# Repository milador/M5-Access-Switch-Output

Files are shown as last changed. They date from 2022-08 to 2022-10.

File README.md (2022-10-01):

# M5-Access-Switch-Output

A Wi-Fi enabled Adaptive Switch Output device based on ESP32 M5StickC/M5StickCPlus which offers up to two 3.5mm switch outputs. The M5 Switch Output can be used to operate up to two switch adapted devices.

<p align="center">
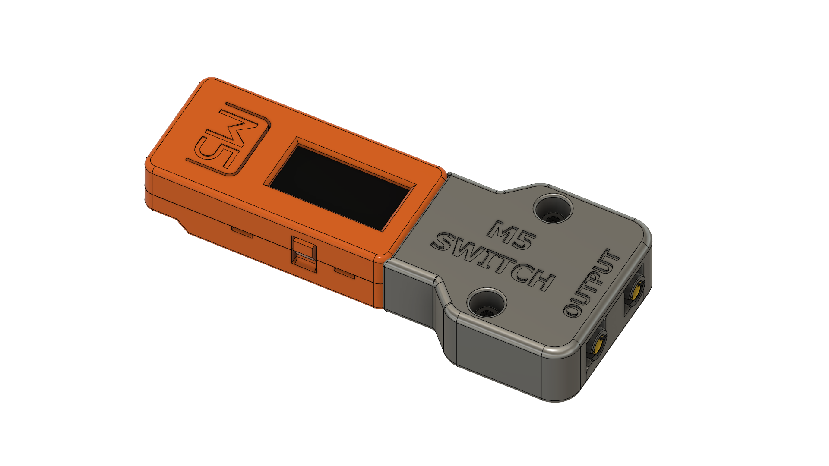
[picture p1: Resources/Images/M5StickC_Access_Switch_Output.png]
M5StickC_Access_Switch_Output

</p>

## Requirements and setup instructions 
The setup process is divided to three main catagories:

  1. [Hardware](./Hardware/) : The required hardware and design files
  2. [Software](./Software/) : The required software
  3. [Documentation](./Documentation/) : The assembly guide,user guide and other documents 

## License

### MIT License

Copyright (c) 2022 milador

Permission is hereby granted, free of charge, to any person obtaining a copy of this software and associated documentation files (the "Software"), to deal in the Software without restriction, including without limitation the rights to use, copy, modify, merge, publish, distribute, sublicense, and/or sell copies of the Software, and to permit persons to whom the Software is furnished to do so, subject to the following conditions:

The above copyright notice and this permission notice shall be included in all copies or substantial portions of the Software.

THE SOFTWARE IS PROVIDED "AS IS", WITHOUT WARRANTY OF ANY KIND, EXPRESS OR IMPLIED, INCLUDING BUT NOT LIMITED TO THE WARRANTIES OF MERCHANTABILITY, FITNESS FOR A PARTICULAR PURPOSE AND NONINFRINGEMENT. IN NO EVENT SHALL THE AUTHORS OR COPYRIGHT HOLDERS BE LIABLE FOR ANY CLAIM, DAMAGES OR OTHER LIABILITY, WHETHER IN AN ACTION OF CONTRACT, TORT OR OTHERWISE, ARISING FROM, OUT OF OR IN CONNECTION WITH THE SOFTWARE OR THE USE OR OTHER DEALINGS IN THE SOFTWARE.

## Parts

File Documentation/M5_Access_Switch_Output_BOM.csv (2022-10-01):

Index | Quantity | Component | Digikey Part Number | Manufacturer Part Number | Description | Unit Price (CAD) | Price (CAD) | Link
1 | 1 |  | 2221-K016-P-ND | K016-P | M5STICKC PLUS ESP32-PICO IOT KIT | 31.48 | 31.48 | https://www.digikey.ca/en/products/detail/m5stack-technology-co-ltd/K016-P/13148797
2 | 2 | SW1,SW2 | CP-43514-ND | SJ-43514 | CONN JACK 4COND 3.5MM | 1.48 | 2.96 | https://www.digikey.ca/en/products/detail/SJ-43514/CP-43514-ND/368146
3 | 2 | K1,K2 | Z5417-ND | G3VM-41AY1 | SSR RELAY SPST-NO 2A 0-40V | 5.54 | 11.08 | https://www.digikey.ca/en/products/detail/omron-electronics-inc-emc-div/G3VM-41AY1/5799756
4 | 1 | JP1 | 609-3321-ND | 68016-208HLF | CONN HEADER R/A 8POS 2.54MM | 0.7 | 0.7 | https://www.digikey.ca/en/products/detail/amphenol-cs-fci/68016-208HLF/1878499
5 | 2 | R1,R2 | S220QCT-ND | CFM14JT220R | RES 220 OHM 5% 1/4W AXIAL | 0.15 | 0.3 | https://www.digikey.ca/en/products/detail/stackpole-electronics-inc/CFM14JT220R/1742139
6 | 2 | N/A | 145-50M025045P006-ND | 50M025045P006 | PAN PHILLIPS SCREW, M2.5 X 4.5 T | 0.23 | 0.46 | https://www.digikey.ca/en/products/detail/essentra-components/50M025045P006/11638590
7 | 2 | N/A | 36-9600-ND | 9600 | HEX NUT 1/4" STEEL 4-40 | 0.16 | 0.32 | https://www.digikey.ca/en/products/detail/keystone-electronics/9600/2746248
 |  |  |  |  |  | Total Price (CAD) | 46.52

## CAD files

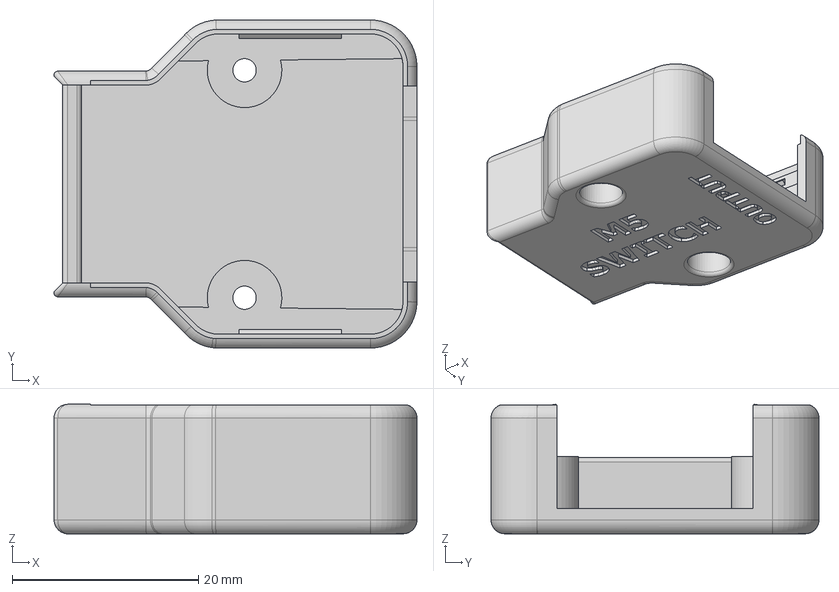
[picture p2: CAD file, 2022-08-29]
Hardware/Case/STEP/M5StickC_Switch_Output_Main.step
38.9 x 35.2 x 13.9 mm

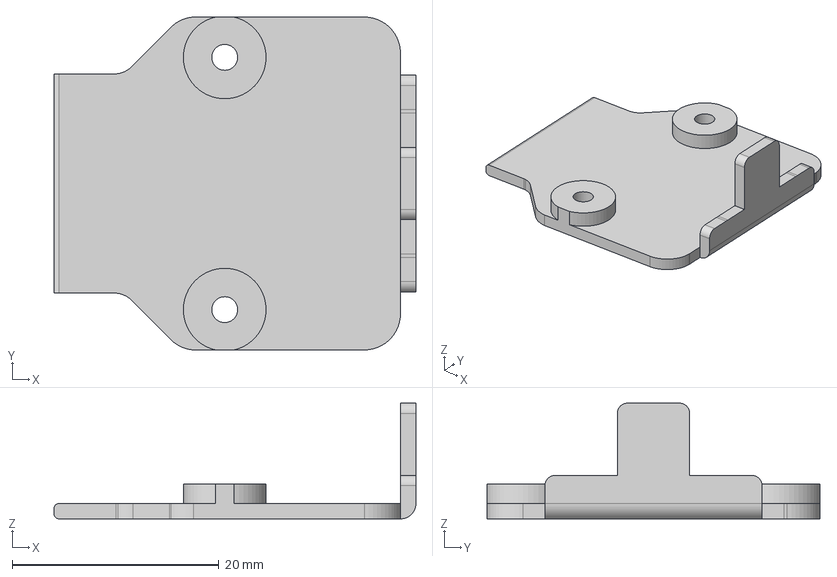
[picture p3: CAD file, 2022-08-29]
Hardware/Case/STEP/M5StickC_Switch_Output_Bottom.step
35.0 x 32.2 x 11.2 mm

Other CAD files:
Hardware/Case/STL/M5StickC_Switch_Output_Bottom.stl
Hardware/Case/STL/M5StickC_Switch_Output_Main.stl

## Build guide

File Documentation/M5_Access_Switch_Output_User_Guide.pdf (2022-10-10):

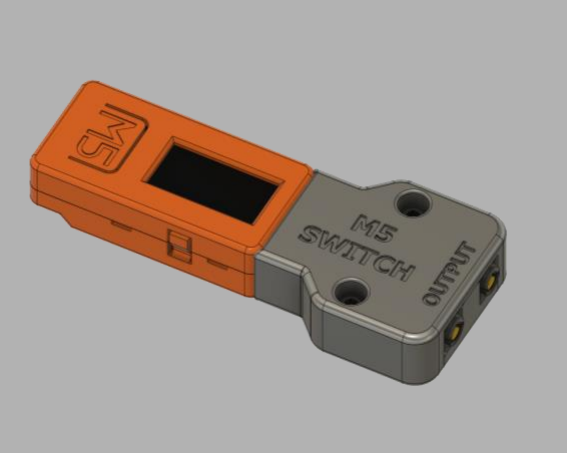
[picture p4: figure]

# M5 ACCESS SWITCH OUTPUT USER GUIDE (V1.0)

A wireless switch output device

### Milad Hajihassan

https://github.com/milador/M5-Access-Switch-Output

1

## Contents

Usage requirements | 2
Usage Components | 2
Usage Process | 2
How to Use? | 2
Sleep Mode | 2

2

## Usage requirements

### Usage Components

1. Mono Audio Jack Cable x 2

## Usage Process

### How to Use?

1. Connect the Switch Output module through two 3.5mm Mono Audio jack cables to two

adapted devices.

1.1. Switch A
1.2. Switch B
2. Connect to the Access Point (Example: Windows 10 PC)

On Windows 10:

2.1. Select Start > Settings > Network & Internet > Show available networks. Select

M5SwitchOutput network and click on connect. The default network password is

12345678.

3. M5StackC will display an IP address on its display screen.
4. Open your favourite web browser software.
5. Enter the IP address from step 3 to access switch output control web page.
6. You can now send switch actions by pressing each switch button.

Sleep Mode

The device goes to sleep mode if it’s not used for more than one minute and automatically wakes up every 3 minutes.

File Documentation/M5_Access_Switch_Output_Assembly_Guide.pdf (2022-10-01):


# M5 ACCESS SWITCH OUTPUT ASSEMBLY GUIDE (V1.0)

A wireless switch output device

### Milad Hajihassan

https://github.com/milador/M5-Access-Switch-Output

1

## Contents

Components List | 2
Software | 3
Installing Arduino IDE | 3
Installing Arduino Libraries | 3
Board Support Packages | 3
Required Software and libraries | 3
Uploading Software | 4
Hardware Assembly | 5
Enclosure design | 5
M5 Access Switch Output Assembly | 6

2

## Components List

1. M5STICKC PLUS ESP32-PICO IOT KIT x 1
2. SJ-43514 3.5MM TRRS AUDIO JACK x 2
3. G3VM-41AY1 SSR RELAY x 2
4. 8 POSITION MALE RIGHT ANGLE HEADER x 1
5. 220 OHM 1/4W RESISTOR x 2
6. M2.5 SCREW (8MM) x 2
7. M2.5 SCREW NUT x 2

The bill of materials can also be downloaded from GitHub repository under main directory. (https://github.com/milador/M5-Access-Switch-Output/blob/main/Documentation/M5_Access_Switch_Output_BOM.csv)

https://github.com/milador/M5-Access-Switch-

Output/blob/main/Documentation/M5_Access_Switch_Output_BOM.csv

3

## Software

The Switch Output software can be downloaded from the GitHub repository under software directory.

https://raw.githubusercontent.com/milador/M5-Access-Switch-Output/main/Software/M5_Access_Switch_Output_Software/M5_Access_Switch_Output_Software.ino (https://raw.githubusercontent.com/milador/M5-Access-Switch-Output/main/Software/M5_Access_Switch_Output_Software/M5_Access_Switch_Output_Software.ino)

### Installing Arduino IDE

The Arduino IDE is required to compile and upload the source code to the MCU in your M5StickC device. You can download and install the Arduino from official Arduino website that you can find using following link:

https://www.arduino.cc/en/software

### Installing Arduino Libraries

The following instructions on how to install additional Arduino libraries helps you to get started with setting up Arduino IDE with required libraries and dependencies.

https://www.arduino.cc/en/guide/libraries

Board Support Packages
You can find the official instructions to install Board Support Packages on M5Stack website using following link:

https://docs.m5stack.com/en/quick_start/m5stickc/arduino

Alternatively, you can perform following instructions to install Board Support Packages:

1. Open and start the Arduino IDE.
2. Go to File > Preferences.
3. Add following link as a new line under Additional Board Manager URLs
- https://m5stack.oss-cnshenzhen.aliyuncs.com/resource/arduino/package_m5stack_index.json (https://m5stack.oss-cn-shenzhen.aliyuncs.com/resource/arduino/package_m5stack_index.json)
4. Restart the Arduino IDE
5. Open the Boards Manager option from the Tools > Board menu and install M5Stack by M5Stack official
6. Wait until the IDE finishes installing the cross-compiling toolchain and tools associated with Board Support Package. This may take few minutes.
7. That’s it! The installation of Board Support Packages is finished.

Required Software and libraries
The software requirements:
- M5_Access_Switch_Output_Software.ino (https://raw.githubusercontent.com/milador/M5-Access-Switch-Output/develop/Software/M5_Access_Switch_Output_Software/M5_Access_Switch_Output_Software.ino)
- M5StickC Plus (https://github.com/m5stack/M5StickC-Plus)

You can use the following instructions to download and install the required libraries:

1) Visit the M5StickC-Plus library github repository page.
2) Click on Code > Download Zip to download M5StickC-Plus.

4

3) Extract M5StickC-Plus-master.zip file
4) Rename M5StickC-Plus-master folder to M5StickC-Plus folder under M5StickC-Plus-master subdirectory.
5) Copy or move M5StickC-Plus folder to Arduino installation library subdirectory. As an example: This is found under C:\Program Files (x86)\Arduino\libraries in windows 10.
6) Visit the M5_Access_Switch_Output_Software.ino raw source code file under Software directory.
7) Right click on the source code or any place on this page and select Save Page As…
8) Select the directory you would like to save the software in your computer.
9) Change File name from M5_Access_Switch_Output_Software to M5_Access_Switch_Output_Software.ino
10) Change Save as type to All Files.
11) Click on Save button.
12) Open the directory you selected in step 8.
13) Double left click or open M5_Access_Switch_Output_Software file
14) Arduino IDE will ask your permission to create a new sketch folder named M5_Access_Switch_Output_Software and move M5_Access_Switch_Output_Software.ino under this folder.
15) Click on the Ok button.
16) Arduino IDE should now open the M5_Access_Switch_Output_Software.ino file automatically.

Uploading Software
Note: Make sure all files are included in your local copy of Software directory before uploading it to the M5StickC device. The libraries can be installed in Arduino libraries.

You can go ahead and upload the downloaded M5_Access_Switch_Output_Software.ino code to M5StickC using Arduino IDE once all the necessary libraries are installed.

1. Start the Arduino IDE
2. Open M5_Access_Switch_Output_Software.ino
3. Select the Board under Tools > Board > M5Stick Arduino Boards as M5Stick-C-Plus
4. Select the correct port number under Tools > Port which should show COM XX (M5Stick-C-Plus)

Note: It’s very important to make sure the correct Board and port number are selected as selecting the wrong board may result problems with bootloader of M5StickC device.

5. Press the Verify button to make sure there is no problem with the software and libraries.
6. Press Upload button

You can now go ahead and upload the software. Arduino IDE will show you a Done Uploading message indicating the software is uploaded to your M5StickC device.

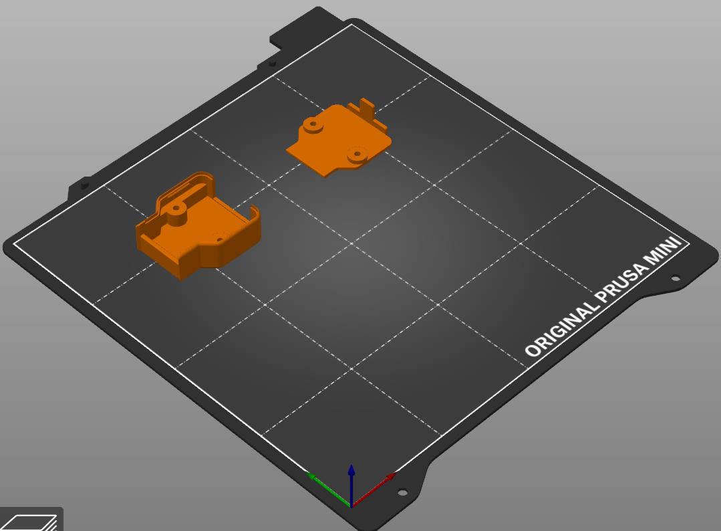
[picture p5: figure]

5

## Hardware Assembly

### Enclosure design

The enclosure/housing files in STL format can be downloaded from GitHub repository under Hardware and Case subdirectory.

- M5StickC_Switch_Output_Main.STL
- M5StickC_Switch_Output_Bottom.STL

https://github.com/milador/M5-Access-Switch-Output/tree/main/Hardware/Case/STL

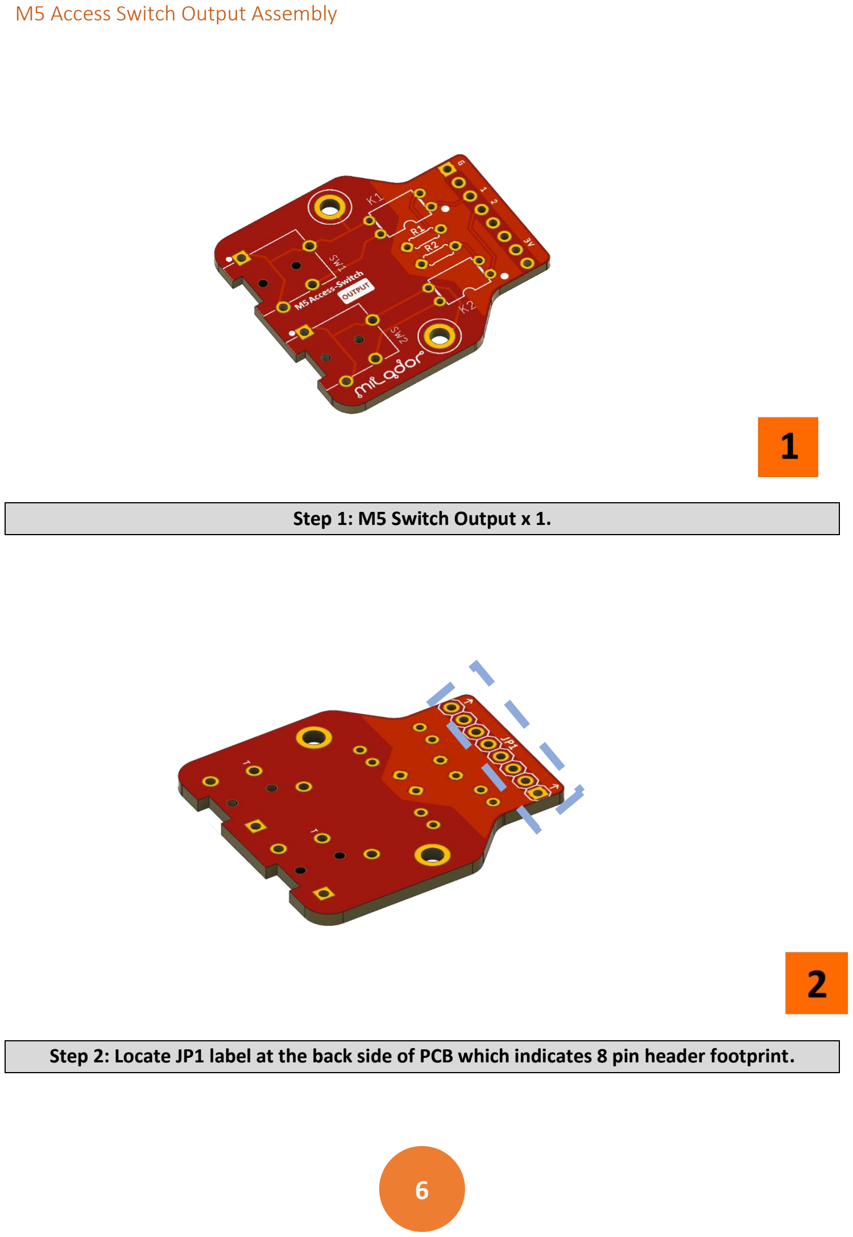
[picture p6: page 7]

6

### M5 Access Switch Output Assembly

Step 1: M5 Switch Output x 1.
Step 2: Locate JP1 label at the back side of PCB which indicates 8 pin header footprint.

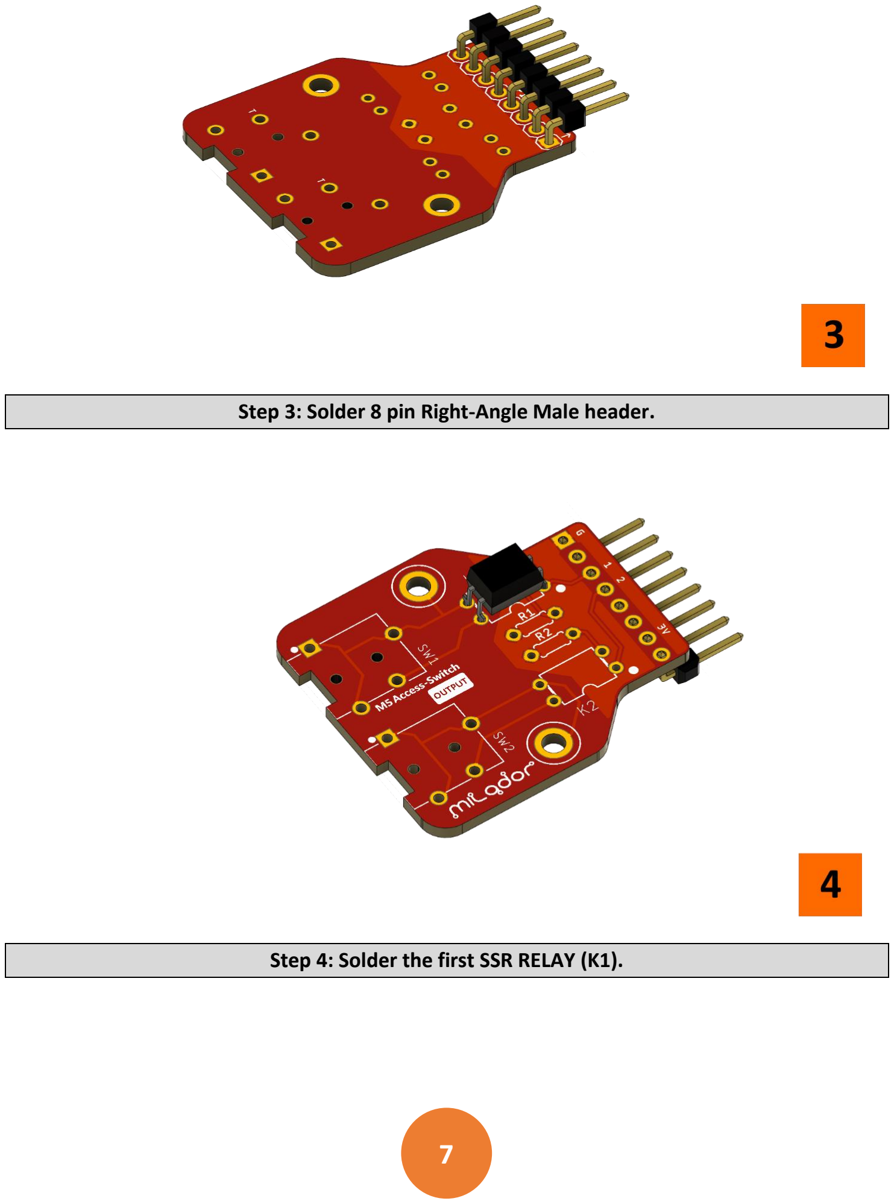
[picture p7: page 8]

7

Step 3: Solder 8 pin Right-Angle Male header.
Step 4: Solder the first SSR RELAY (K1).

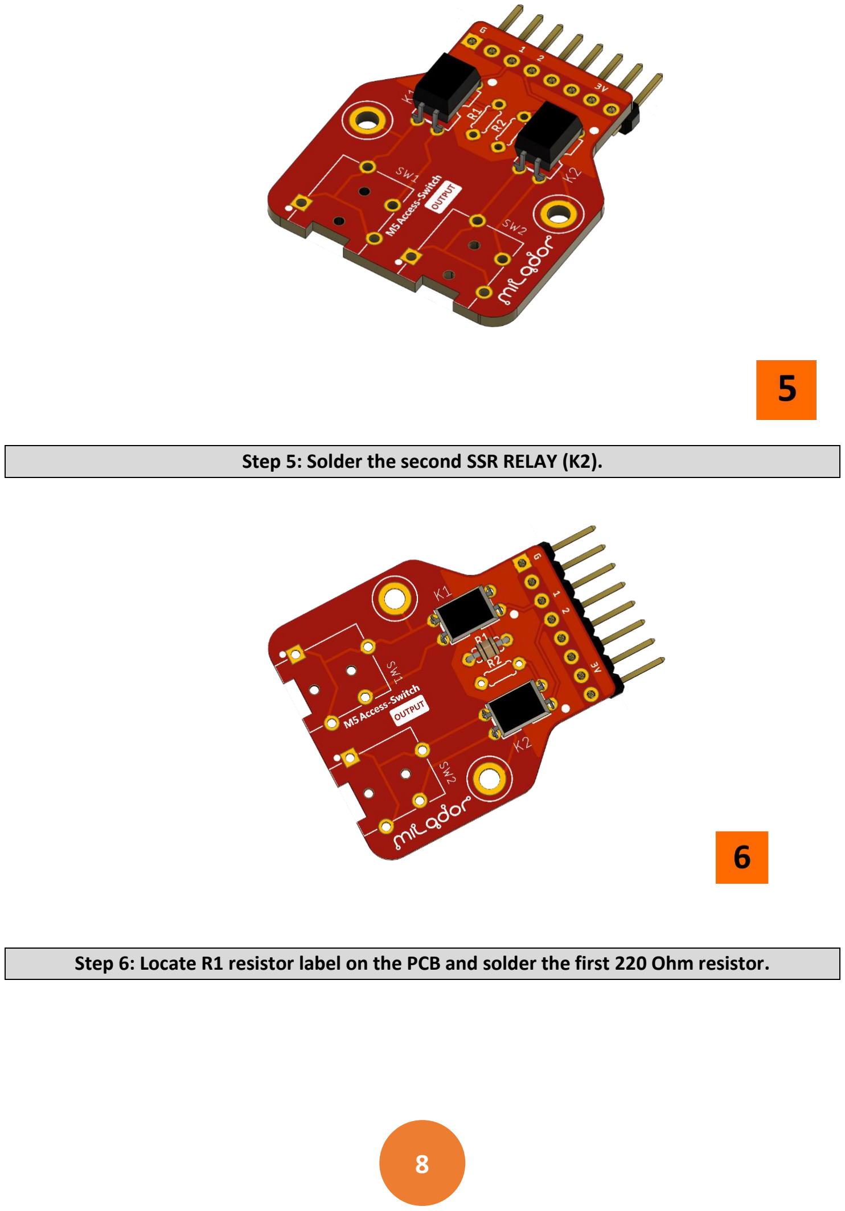
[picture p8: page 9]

8

Step 5: Solder the second SSR RELAY (K2).
Step 6: Locate R1 resistor label on the PCB and solder the first 220 Ohm resistor.

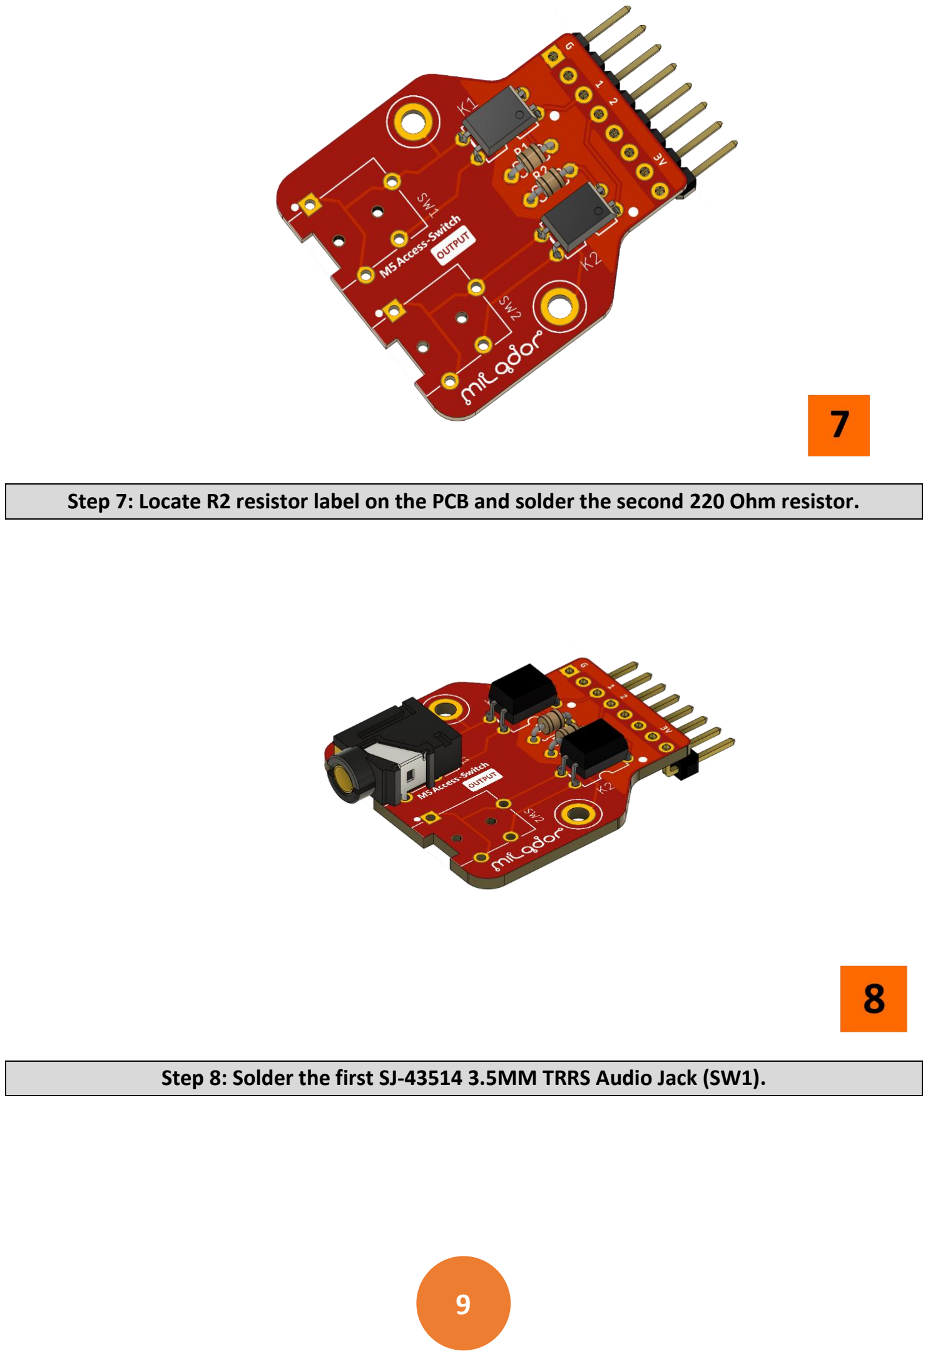
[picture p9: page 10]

9

Step 7: Locate R2 resistor label on the PCB and solder the second 220 Ohm resistor.
Step 8: Solder the first SJ-43514 3.5MM TRRS Audio Jack (SW1).

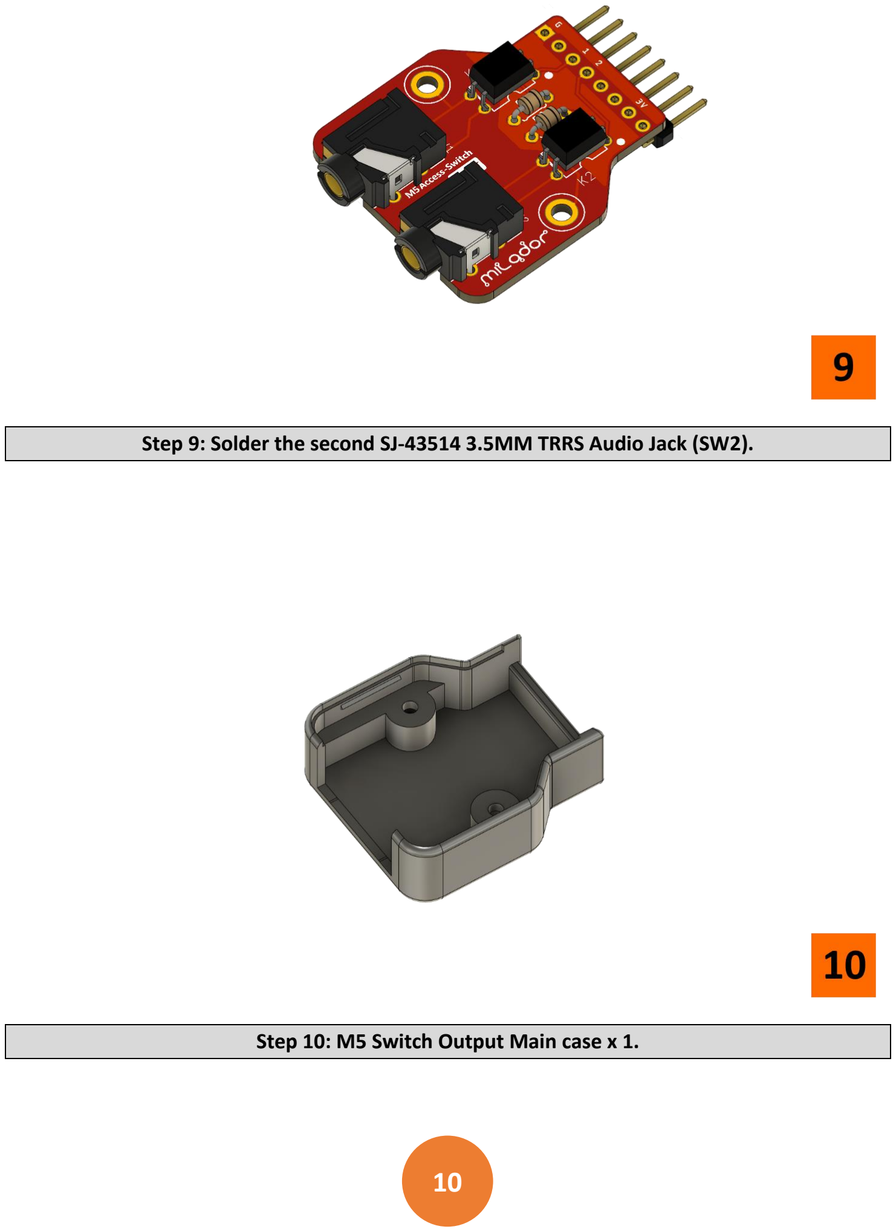
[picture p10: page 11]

10

Step 9: Solder the second SJ-43514 3.5MM TRRS Audio Jack (SW2).
Step 10: M5 Switch Output Main case x 1.

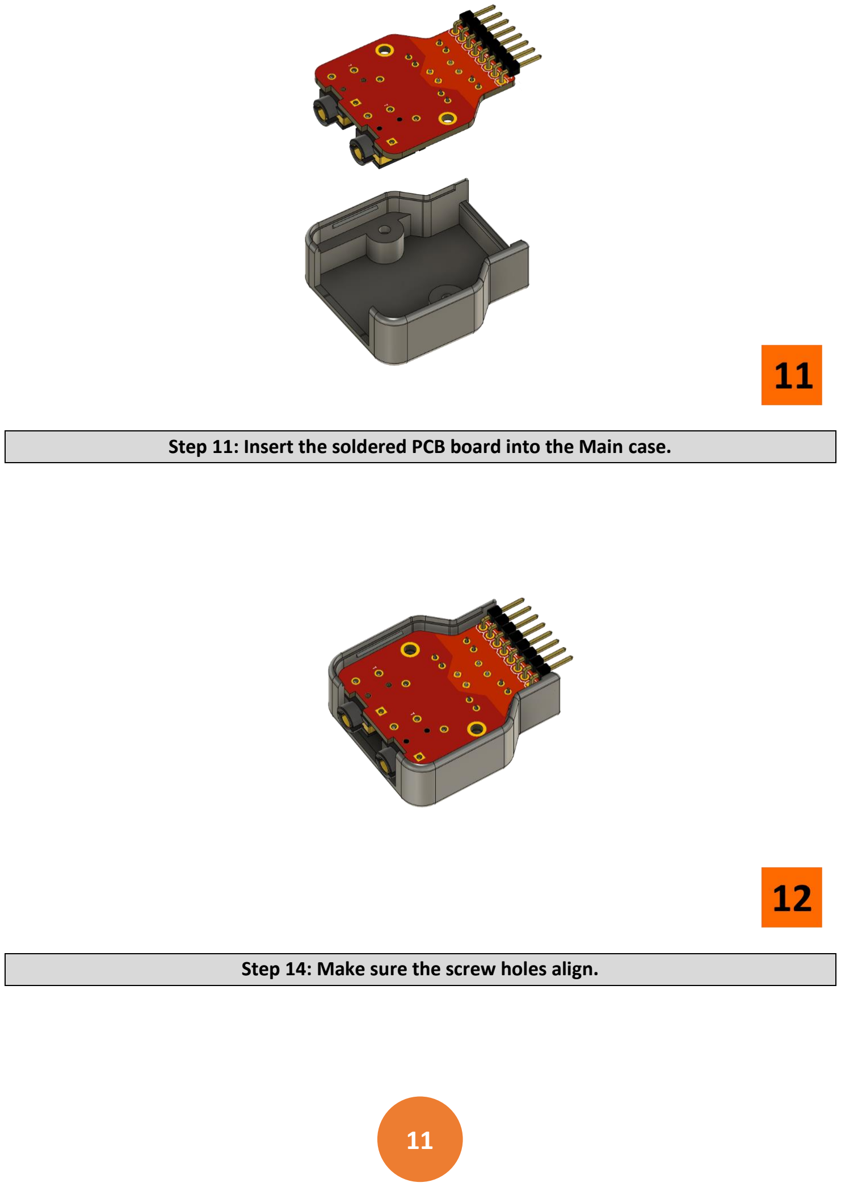
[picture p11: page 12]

11

Step 11: Insert the soldered PCB board into the Main case.
Step 14: Make sure the screw holes align.

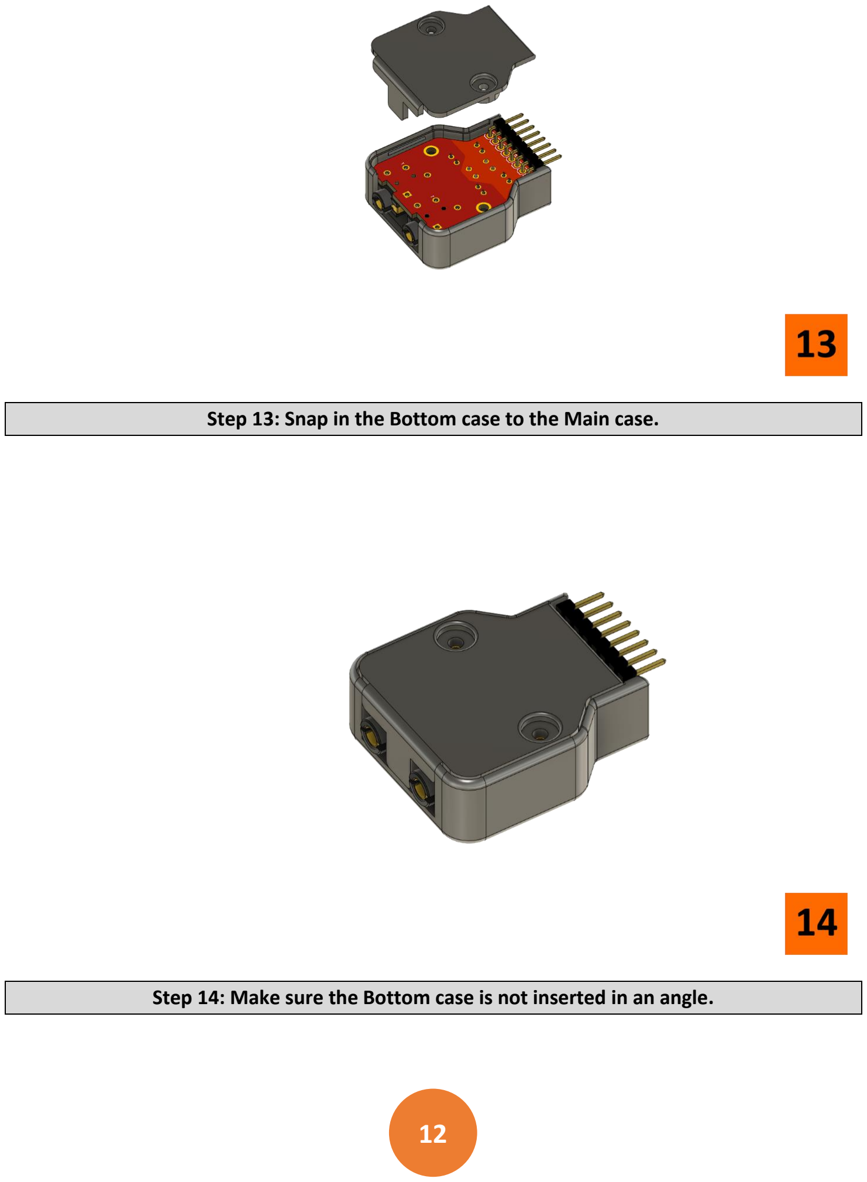
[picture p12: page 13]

12

Step 13: Snap in the Bottom case to the Main case.
Step 14: Make sure the Bottom case is not inserted in an angle.

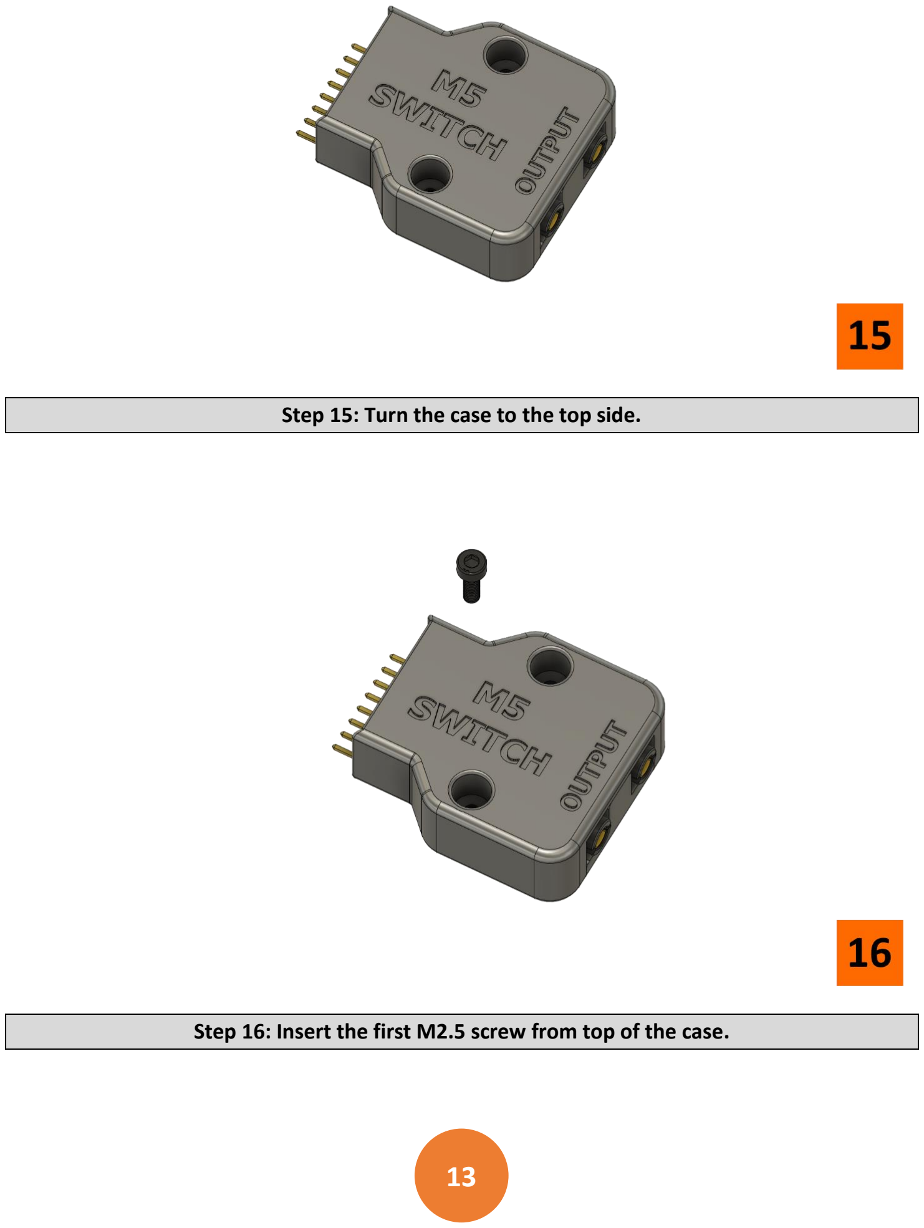
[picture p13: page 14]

13

Step 15: Turn the case to the top side.
Step 16: Insert the first M2.5 screw from top of the case.

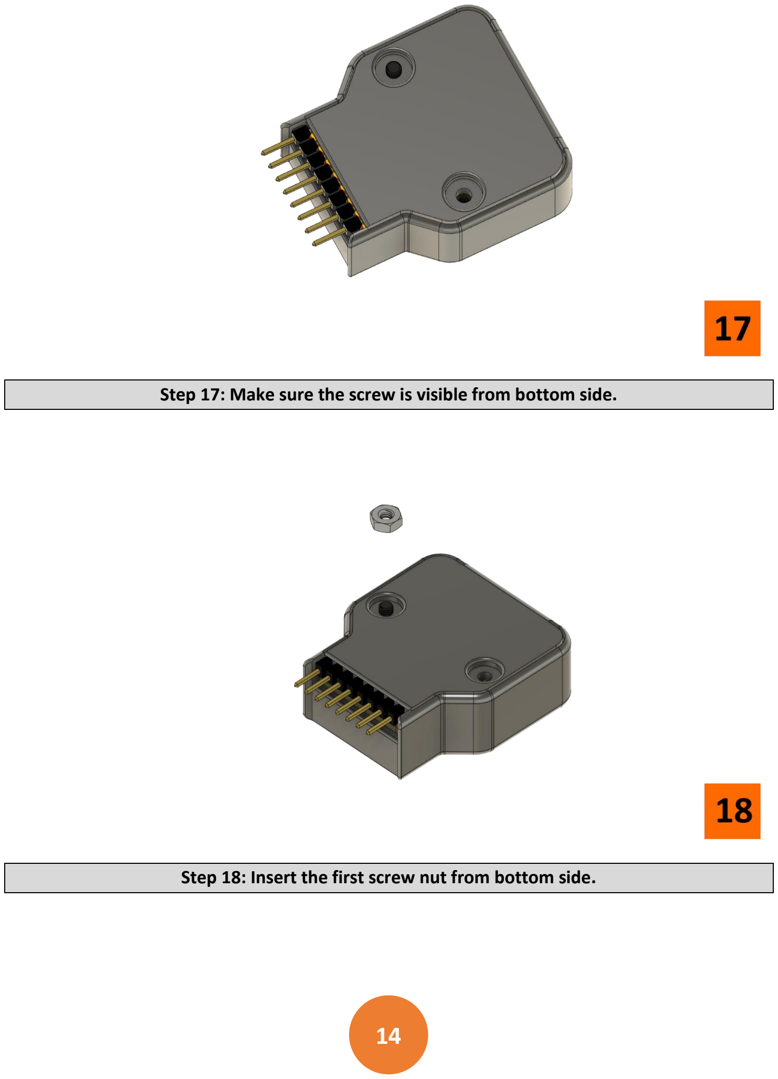
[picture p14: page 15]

14

Step 17: Make sure the screw is visible from bottom side.
Step 18: Insert the first screw nut from bottom side.

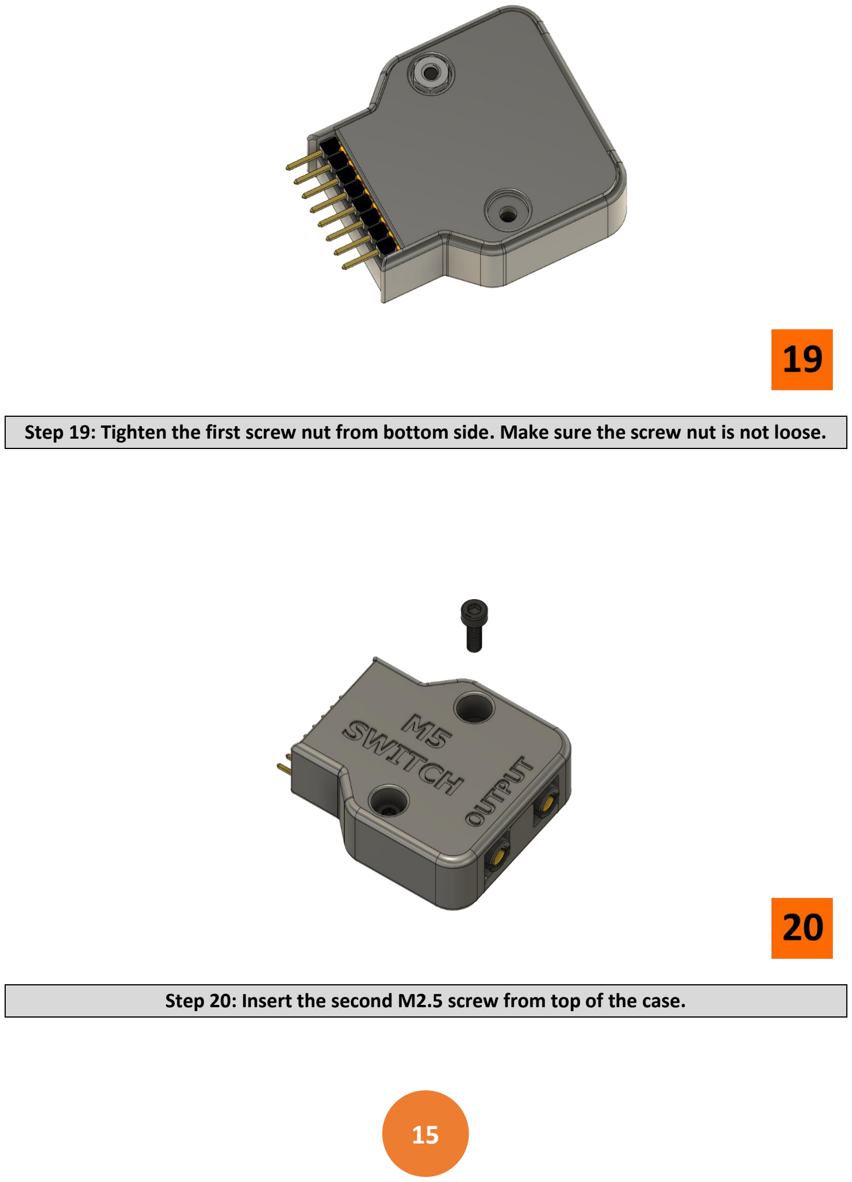
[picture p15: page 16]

15

Step 19: Tighten the first screw nut from bottom side. Make sure the screw nut is not loose.
Step 20: Insert the second M2.5 screw from top of the case.

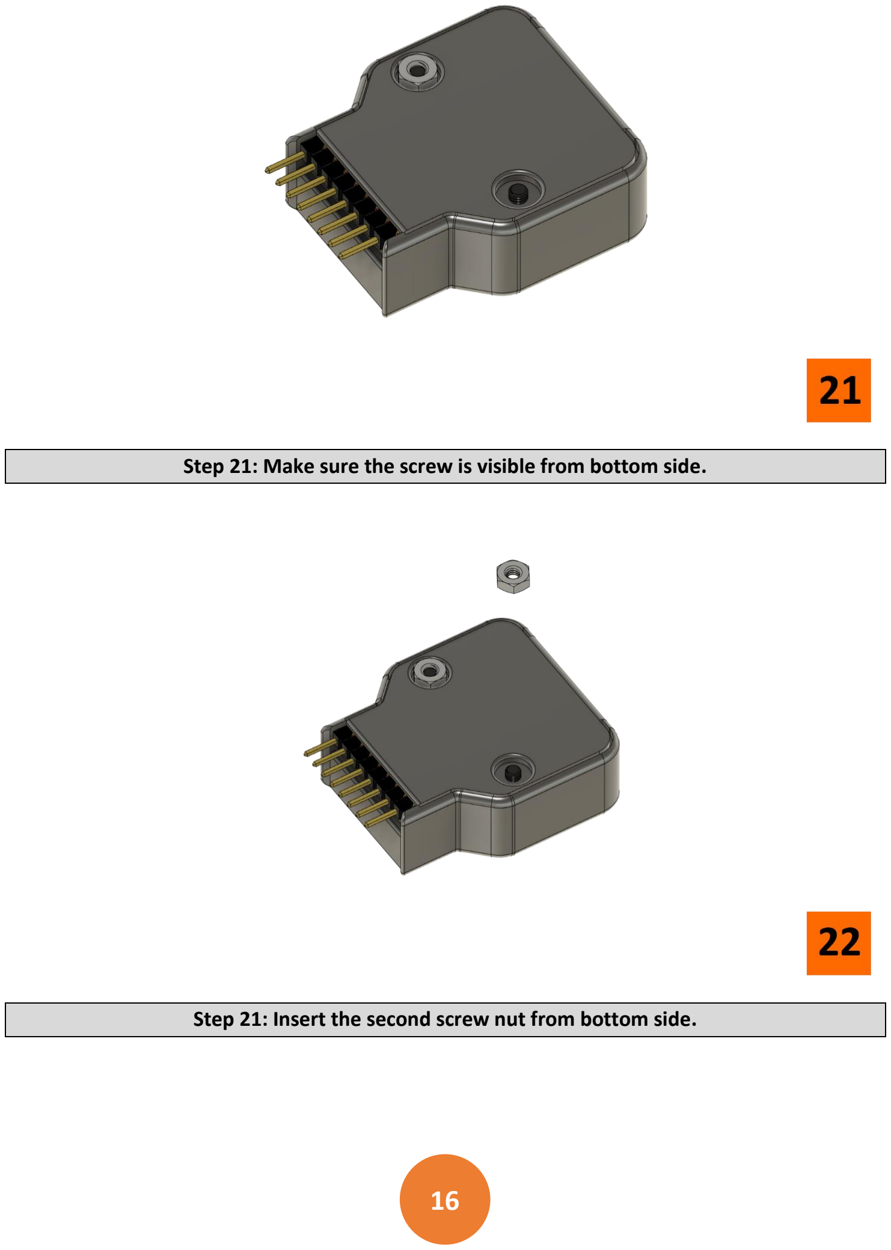
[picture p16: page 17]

16

Step 21: Make sure the screw is visible from bottom side.
Step 21: Insert the second screw nut from bottom side.

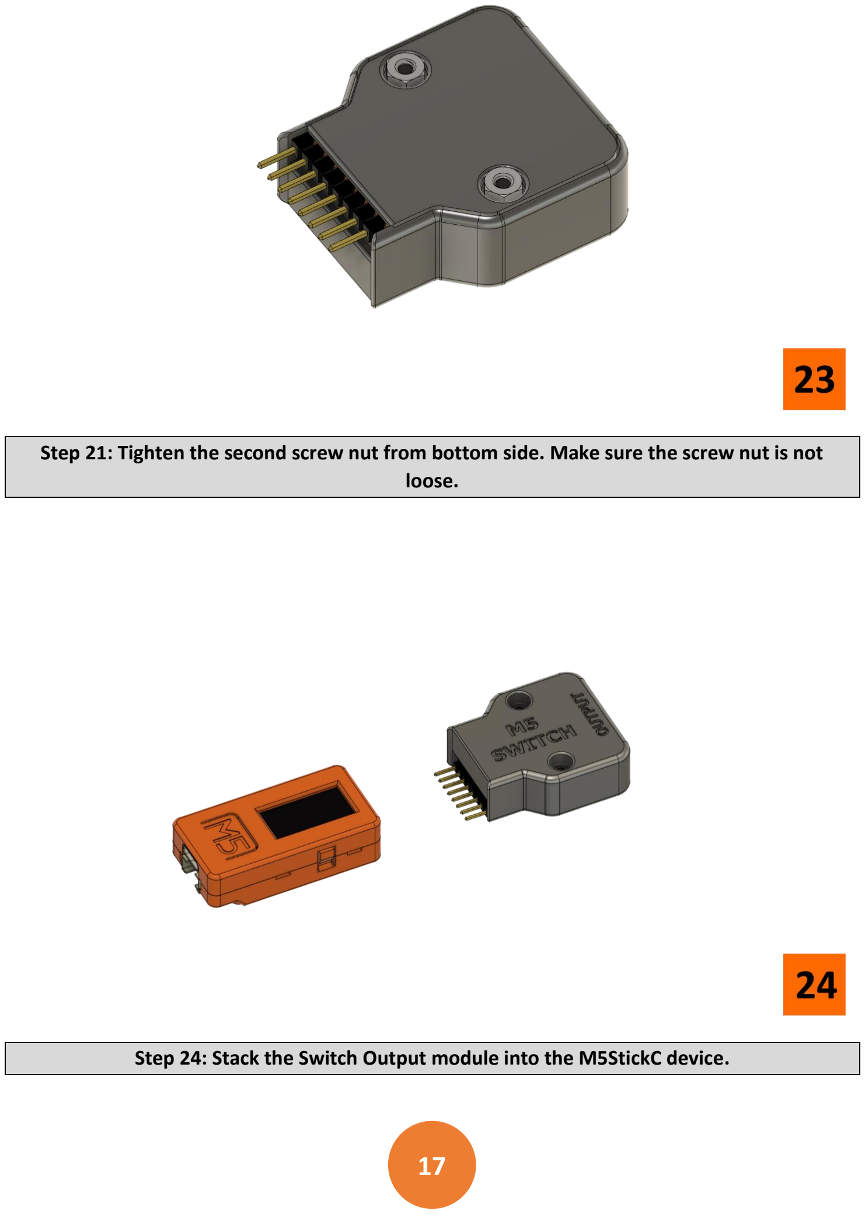
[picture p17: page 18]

17

Step 21: Tighten the second screw nut from bottom side. Make sure the screw nut is not loose.
Step 24: Stack the Switch Output module into the M5StickC device.

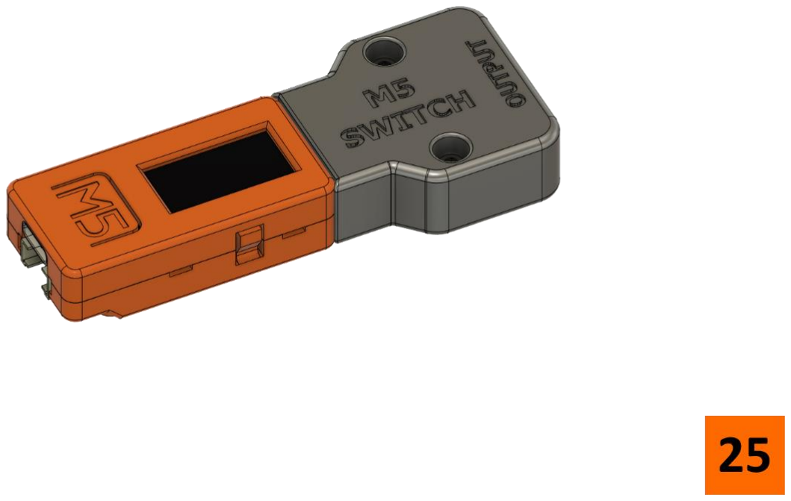
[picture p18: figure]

18

Step 25: That’s it! The assembly process is complete.

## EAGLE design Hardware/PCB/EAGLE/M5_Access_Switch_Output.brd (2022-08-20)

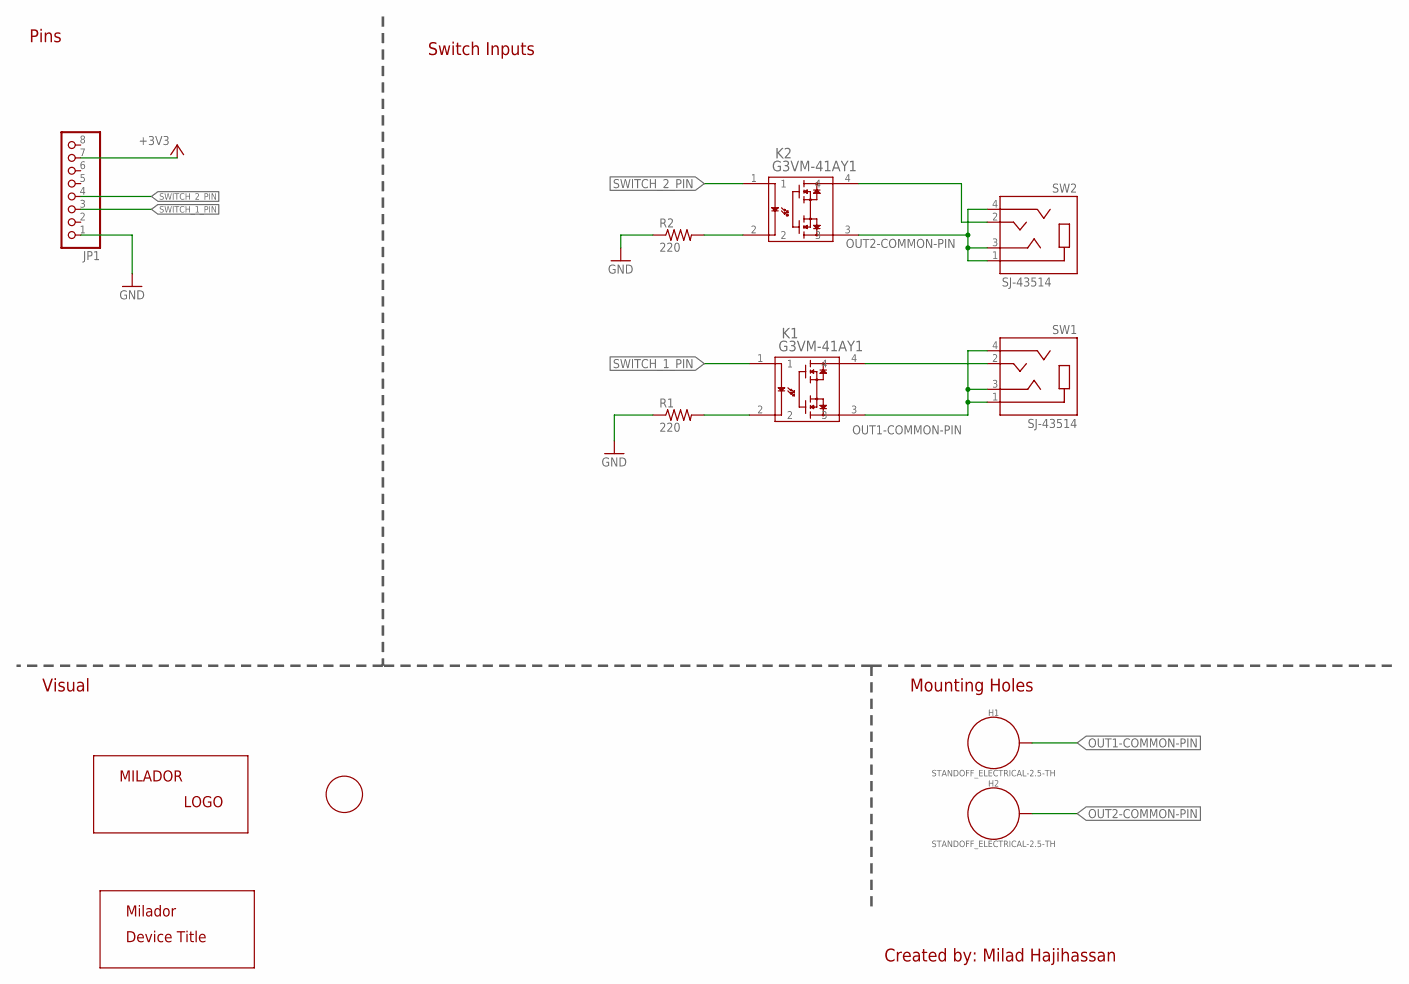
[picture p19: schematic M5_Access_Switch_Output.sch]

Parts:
H1, H2: STANDOFF_ELECTRICAL-2.5-TH; STANDOFF-ELECTRICAL-2.5-TH
JP1: HEADER_MALE-1X8ROUND-RA; 1X08_ROUND_RA
K1, K2: G3VM-41AY1; A-DIP4_THD_OMR
LABEL_DEVICE_TOP: MILADOR-DEVICE-M5-ACCESS-SWITCH; MILADOR_M5_ACCESS_SWITCH
LABEL_LOGO_TOP: MILADOR-LOGO-SM; MILADOR_LOGO2
LABEL_OUTPUT_TOP: MILADOR-SWITCH-NAME-SW-OUTPUT; SWITCH-OUTPUT
R1, R2: 220; RESISTOR_0204/5
SW1, SW2: SJ-43514; CUI_SJ-43514

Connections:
+3V3: JP1.7
GND: JP1.1, R1.1, R2.1
unnamed: K2.2, R2.2
unnamed: K1.2, R1.2
OUT1-COMMON-PIN: H1.P1, K1.3, SW1.1 (SLEEVE), SW1.3 (RING1), SW1.4 (RING2)
OUT2-COMMON-PIN: H2.P1, K2.3, SW2.1 (SLEEVE), SW2.3 (RING1), SW2.4 (RING2)
OUT-1-PIN: K2.4, SW2.2 (TIP)
OUT-2-PIN: K1.4, SW1.2 (TIP)
SWITCH_1_PIN: JP1.3, K1.1
SWITCH_2_PIN: JP1.4, K2.1

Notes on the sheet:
Switch Inputs
Pins
Mounting Holes
Visual
Created by: Milad Hajihassan

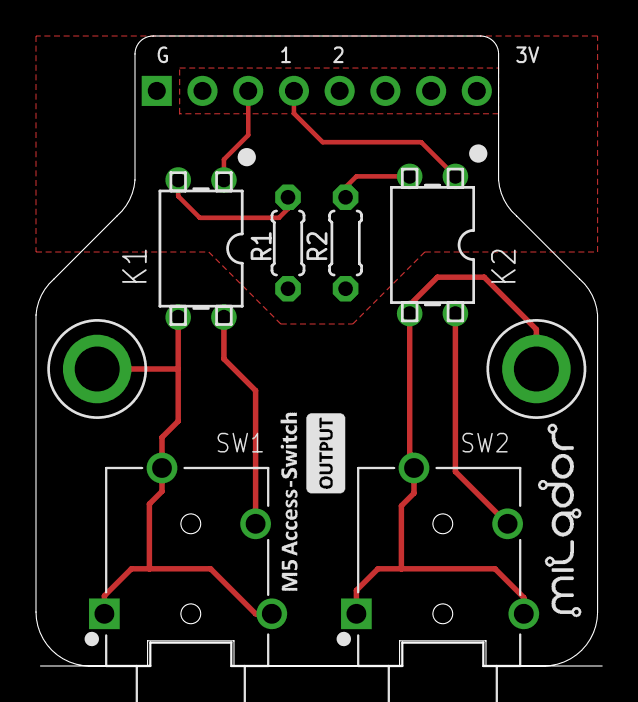
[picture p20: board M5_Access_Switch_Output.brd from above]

Board: 2 copper layers, 31.2 x 35.0 mm, 12 parts (1 on the bottom side), 9 nets.

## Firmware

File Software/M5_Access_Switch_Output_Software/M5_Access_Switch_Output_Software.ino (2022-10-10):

/** ************************************************************************
 * File Name: M5_Access_Switch_Output_Software.ino 
 * Title: M5 Switch Output Interface Software
 * Developed by: Milador
 * Version Number: 1.0 (24/9/2022)
 * Github Link: https://github.com/milador/M5-Access-Switch-Output
 ***************************************************************************/

#include <WiFi.h>
#include <WiFiClient.h>
#include <WiFiAP.h>
#include <M5StickCPlus.h>

#define SWITCH_A_PIN         26
#define SWITCH_B_PIN         25
#define TO_SLEEP_TIME        60        //Go to sleep if no data was sent in 60 seconds
#define TO_WAKE_TIME         180       //Wake up every 3 minutes 
#define S_TO_MS_FACTOR       1000
#define US_TO_S_FACTOR       1000000
#define SLEEP_MODE_ENABLED   true      //Set to false to disable sleep mode

// Set these to your desired credentials.
const char *ssid = "M5SwitchOutput";
const char *password = "12345678";

String g_switchMessage;        //Custom message 
int g_pageNumber;
unsigned long currentTime = 0, switchDataTime = 0;


WiFiServer server(80);


void setup() {
  
  pinMode(SWITCH_A_PIN, OUTPUT);
  pinMode(SWITCH_B_PIN, OUTPUT);

  Serial.begin(115200);
  M5.begin();                                                                  //Starts M5Stack
  Serial.println();
  Serial.println("Configuring access point...");

  // You can remove the password parameter if you want the AP to be open.
  WiFi.softAP(ssid, password);
  IPAddress myIP = WiFi.softAPIP();
  Serial.print("AP IP address: ");
  Serial.println(myIP);
  server.begin();
  Serial.println("Server started");
  showIntro();                                                                 //Show intro page
  delay(5);   
  showMode(myIP);
  delay(5000);
  initBatterySaver();
}

void loop() {

  if(SLEEP_MODE_ENABLED) { batterySaver(); } // Sleep mode          
  WiFiClient client = server.available();   // listen for incoming clients

  if (client) {                             // if you get a client,
    Serial.println("New Client.");          // print a message out the serial port
    String currentLine = "";                // make a String to hold incoming data from the client
    while (client.connected()) {            // loop while the client's connected
      if (client.available()) {             // if there's bytes to read from the client,
        char c = client.read();             // read a byte, then
        Serial.write(c);                    // print it out the serial monitor
        if (c == '\n') {                    // if the byte is a newline character

          // if the current line is blank, you got two newline characters in a row.
          // that's the end of the client HTTP request, so send a response:
          if (currentLine.length() == 0) {
            // HTTP headers always start with a response code (e.g. HTTP/1.1 200 OK)
            // and a content-type so the client knows what's coming, then a blank line:
            client.println("HTTP/1.1 200 OK");
            client.println("Content-type:text/html");
            client.println();
            client.print("<head><style>.center {display: flex; justify-content: center; align-items: center; height: 200px; border: 3px solid blue; }</style></head>");
            // the content of the HTTP response follows the header:
            //client.print("Click <a href=\"/A\">here</a> to activate Switch A.<br>");
            //client.print("Click <a href=\"/B\">here</a> to activate Switch B.<br>");
            client.print("<h2 style=\"text-align:center\">M5StickC Switch Output Interface</h2><br>");
            client.print("<div class=\"center\"><button onclick=\"location.href='/A'\" style=\"height:200px;width:200px\" type=\"button\">Switch A</button>");
            client.print("<button onclick=\"location.href='/B'\" style=\"height:200px;width:200px\" type=\"button\">Switch B</button></div><br>");
            client.print("<p style=\"text-align:center\">More information at milador.ca</p><br>");

            // The HTTP response ends with another blank line:
            client.println();
            // break out of the while loop:
            break;
          } else {    // if you got a newline, then clear currentLine:
            currentLine = "";
          }
        } else if (c != '\r') {  // if you got anything else but a carriage return character,
          currentLine += c;      // add it to the end of the currentLine
        }

        // Check to see if the client request was "GET /A" or "GET /B":
        if (currentLine.endsWith("GET /A")) {
          digitalWrite(SWITCH_A_PIN, HIGH);
          delay(100);
          digitalWrite(SWITCH_A_PIN, LOW);
        }
        if (currentLine.endsWith("GET /B")) {
          digitalWrite(SWITCH_B_PIN, HIGH);
          delay(100);
          digitalWrite(SWITCH_B_PIN, LOW);
        }
        switchDataTime = millis();  
      }
    }
    // close the connection:
    client.stop();
    Serial.println("Client Disconnected.");
  }
}


//***INITIALIZE BATTERY SAVER FUNCTION***//
void initBatterySaver() {
  esp_sleep_enable_ext0_wakeup(GPIO_NUM_37,LOW);
  esp_sleep_enable_ext0_wakeup(GPIO_NUM_39,LOW);
  currentTime = switchDataTime = millis();
}

//***BATTERY SAVER FUNCTION***//
void batterySaver() {
  currentTime = millis();
  if (currentTime > (switchDataTime + (TO_SLEEP_TIME * S_TO_MS_FACTOR))) {
    M5.Axp.DeepSleep(SLEEP_SEC(TO_WAKE_TIME));
  }
}

//*** SHOW INTRO PAGE***//
void showIntro() {

  g_pageNumber = 0;                                  //Set intro page number 

  M5.Lcd.setRotation(3);

  M5.Lcd.fillScreen(WHITE);
  delay(200);
  M5.Lcd.fillScreen(RED);
  delay(200);
  M5.Lcd.fillScreen(GREEN);
  delay(200);
  M5.Lcd.fillScreen(BLUE);
  delay(200);
  M5.Lcd.fillScreen(BLACK);
  
  M5.Lcd.setTextColor(WHITE);

  M5.Lcd.setTextSize(2);                        
  M5.Lcd.drawCentreString("Milador.ca",130,40,2);

  M5.Lcd.setTextSize(1);
  M5.Lcd.drawCentreString("M5Stick Switch Output",130,80,1);

  delay(3000);
}

//*** SHOW MODE PAGE***//
void showMode(IPAddress ip){

  g_pageNumber = 1;

  M5.Lcd.setRotation(3);
  M5.Lcd.fillScreen(BLACK);                      //Black background
  M5.Lcd.drawRect(2, 2, 238, 30, BLUE);
  M5.Lcd.setTextColor(WHITE);
  M5.Lcd.setTextSize(1);
  M5.Lcd.drawCentreString(ipToString(ip),120,5,4);
  
  showModeInfo();
  showMessage();
}

String ipToString(IPAddress ip){
  String s="";
  for (int i=0; i<4; i++)
    s += i  ? "." + String(ip[i]) : String(ip[i]);
  return s;
}

//*** SHOW MODE INFO***//
void showModeInfo() {

  String switchAText = "Swich A";
  String switchBText = "Swich B";
  M5.Lcd.setRotation(3);
  M5.Lcd.drawRect(2, 35, 238, 62, WHITE);
  M5.Lcd.setTextColor(WHITE); 
  M5.Lcd.setTextSize(1);

  M5.Lcd.drawCentreString(switchAText,120,44,2);
  M5.Lcd.drawCentreString(switchBText,120,67,2);
}

//*** SHOW CUSTOM MESSAGE***//
void showMessage() {

  M5.Lcd.setRotation(3);
  M5.Lcd.setTextSize(1);                    // Select the font
  //Display connection status based on code
  M5.Lcd.drawRect(2, 100, 238, 30, BLUE);
  M5.Lcd.setTextColor(BLUE); 
  g_switchMessage = "Switch Output";
  Serial.println(g_switchMessage);
  M5.Lcd.drawCentreString(g_switchMessage,120,105,2);// Display message
    
}

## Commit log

2022-08-20 Added Stereo jack design
    [M5_Access_Switch_Output.brd, M5_Access_Switch_Output.sch]
2022-08-20 Updated design to two mono jack design
    [M5_Access_Switch_Output.brd, M5_Access_Switch_Output.sch]
2022-08-29 Added enclosure/case files
    [M5StickC_Switch_Output_Bottom.step, M5StickC_Switch_Output_Bottom.stl, M5StickC_Switch_Output_Main.step, M5StickC_Switch_Output_Main.stl]
2022-08-29 Added BOM
    [M5_Access_Switch_Output_BOM.xlsx]
2022-10-01 Updated BOM file
    [M5_Access_Switch_Output_BOM.csv, M5_Access_Switch_Output_BOM.xlsx]
2022-10-01 Added assembly guide

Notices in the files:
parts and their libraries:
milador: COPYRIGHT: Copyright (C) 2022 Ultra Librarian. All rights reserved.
